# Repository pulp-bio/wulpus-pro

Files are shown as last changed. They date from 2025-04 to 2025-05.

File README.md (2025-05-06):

# WULPUS PRO v0.1.0
## A base platform for Wearable Ultra Low Power Ultrasound

# Introduction

This repository contains the work in progress on the WULPUS PRO ultrasound platform, a successor of the [WULPUS Project](https://github.com/pulp-bio/wulpus)

WULPUS PRO is a compact base platform for an ultra low power ultrasound sensing, featuring the following specifications:
- **16 channels** (time-multiplexed)
- **30 V** unipolar excitations with programmable frequency (100 kHz - 10 MHz)
- **Indirect and Direct Bias** (-30 V up to 30 V) for CMUT transducers
- **30.8 dB** Programable-Gain Amplifier + **80 dB** external VGA
- **Programmable** linear Time Gain Compesation Profiles
- **Optional** Envelope Extractor, runtime configurable
- **8 Msps** Analog-to-Digital converter (12 bit resolution)
- **SPI (8 MHz)** host MCU interface
- **Compactness and light weight** (40 x 20 mm footprint)
- **Ultra-Low Power** consumption of **<25 mW**

# WULPUS PRO system diagram

Work in progress.

# Structure of the repository

This repository has the following folders:

- `fw`, containing the firmware source code, namely:
    - source code for the nRF52832 MCU of the nRF52 DK, located at `fw/nrf52/ble_peripheral/US_probe_nRF52_firmware`
    - source code for the nRF52840 USB dongle, located at `fw/nrf52/peripheral/US_probe_dongle_firmware`
    - source code for the MSP430 ultrasound MCU, located at `fw/msp430`
- `sw`, containing the Python code for the WULPUS Pro Graphical User Interface
 
- `hw`, containing the CAD source files for 
    - WULPUS PRO Acquisition PCB (located at `hw/wulpus_pro_acq_pcb_dev_board`)
    - WULPUS adapter PCB for polyCMUT transducer (located at `hw/wulpus_polycmut_adapter`)

- `docs`, containing the project documentation (Work in Progress)

# Documentation 

WULPUS PRO build up on the top of the original WULPUS platfrom. Therefore, please refer to the original [WULPUS User Manual](docs/wulpus_user_manual.pdf) for assembly instructions, example measurements and GUI overview.

# How to reproduce?

To build and run your own instance of the **WULPUS PRO** platform, follow the steps below:

### 1. Manufacture and Assemble the Hardware

Produce the **WULPUS PRO acquisition development board** using the design files in:

- `hw/wulpus_pro_acq_pcb_dev_board`
- (Optionally) `hw/wulpus_polycmut_adapter`

Assemble the PCB using the provided schematics and BOMs.

### 2. Interconnect with nRF52 DK

Use the following pin mapping to connect the WULPUS PRO acquisition board to the **nRF52 DK**:

| **Signal**         | **nRF52 DK Pin** | **WULPUS PRO Connector Pin** |
|--------------------|------------------|-------------------------------|
| `SPI_SS`           | P0.04            | X3.4                          |
| `SPI_CLK`          | P0.29            | X3.3                          |
| `SPI_MISO`         | P0.30            | X3.1                          |
| `SPI_MOSI`         | P0.31            | X3.2                          |
| `Data_ready`       | P0.24            | X4.2                          |
| `BLE_conn_ready`   | P0.25            | X4.3                          |

### 3. Flash the MSP430 Firmware

Navigate to `fw/msp430/` and follow instructions to:

- Set up Code Composer Studio
- Compile the firmware
- Flash the MSP430 MCU

### 4. Flash the nRF52 DK and USB Dongle

Go to `fw/nrf52/` to:

- Set up Segger Studio and nRF Connect SDK
- Compile and flash:
  - nRF52832 DK (`ble_peripheral`)
  - nRF52840 USB dongle (`peripheral`)

### 5. Set Up the Python GUI

1. [Install Miniconda](https://docs.conda.io/en/latest/miniconda.html)
2. Go to the `sw` folder (contains `requirements.yml`)
3. Open terminal (Anaconda Prompt on Windows), run:
   ```bash
   conda env create -f requirements.yml
   conda activate wulpus_env
   jupyter notebook
   ```

## How to use?

To start a measurement with **WULPUS PRO**, follow these steps:

1. **Plug in the USB dongle** and **power the nRF52 DK** via USB.
2. **Check the dongle connection** (green LED should light up).  
   If not, press the **reset button on the nRF52 DK**, then try again.
3. **Only after confirming** dongle connectivity, **power the WULPUS PRO board** (via connector or debug pin headers).
4. Open a **Conda terminal**, activate the environment:
   ```bash
   conda activate wulpus_env
   ```

5. Then navigate to the `sw/` folder and open `wulpus_pro_gui.ipynb`. Follow the notebook instructions to begin acquisition.

# Authors

The WULPUS Pro system was developed at the [Integrated Systems Laboratory (IIS)](https://iis.ee.ethz.ch/) at ETH Zurich by:
- [Sergei Vostrikov](https://scholar.google.com/citations?user=a0KNUooAAAAJ&hl=en) (PCB design, Firmware, Software, Open-Sourcing)
- [Federico Villani](https://scholar.google.com/citations?user=5LgLMCEAAAAJ&hl=en) (PCB design, Component selection)
- [Cédric Hirschi](https://www.linkedin.com/in/c%C3%A9dric-cyril-hirschi-09624021b/) (Firmware, Software)
- [Andrea Cossettini](https://scholar.google.com/citations?user=d8O91jIAAAAJ&hl=en) (Supervision, Project administration)
- [Luca Benini](https://scholar.google.com/citations?hl=en&user=8riq3sYAAAAJ) (Supervision, Project administration)

Thanks to all the people who contributed to the WULPUS Pro platform:
- [Sebastian Frey](https://scholar.google.com/citations?user=7jhiqz4AAAAJ&hl=en) (Design review)

# License
The following files are released under Apache License 2.0 (`Apache-2.0`) (see `sw/LICENSE`):

- `sw/`

The following files are released under Solderpad v0.51 (`SHL-0.51`) (see `hw/LICENSE`):

- `hw/`

The `fw/msp430/` and `fw/nrf52/` directories contain third-party sources that come with their own
licenses. See the respective folders and source files for the licenses used.

## Limitation of Liability
In no event and under no legal theory, whether in tort (including negligence), contract, or otherwise, unless required by applicable law (such as deliberate and grossly negligent acts) or agreed to in writing, shall any Contributor be liable to You for damages, including any direct, indirect, special, incidental, or consequential damages of any character arising as a result of this License or out of the use or inability to use the Work (including but not limited to damages for loss of goodwill, work stoppage, computer failure or malfunction, or any and all other commercial damages or losses), even if such Contributor has been advised of the possibility of such damages.

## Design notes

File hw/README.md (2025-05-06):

# WULPUS PRO PCB design files
This directory contains the design files for the printed circuit boards (PCBs) of the WULPUS PRO project.
Each subdirectory corresponds to a separate PCB project. Inside you can find the Altium CAD design files:
- Source design files
- PDF schematics and assembly drawings (`docs` folder), 
- Fabrication outputs (`fabrication_outputs` folder):
    - Bill of Materials(.xlsx) 
    - Gerber files
    - NC drill files
    - Pick and Place files

# License
The PCB design files are licensed under Solderpad v0.51 (`SHL-0.51`) license. Please, check the `hw/LICENSE` file for details.

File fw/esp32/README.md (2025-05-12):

# WULPUS PRO ESP32 Firmware

This firmware enables WULPUS PRO to connect to Wi-Fi via a ESP32-C6, which enables higher throughputs and thus framerates.

The firmware includes the following features:
- **mDNS**: Multicast DNS for local network discovery
- **Full integration with the Python API**: The firmware also comes with an extension to the Python API, which allows you to control the WULPUS PRO over Wi-Fi
- **Power Management**: The firmware includes power management, which allows the ESP32 to enter light sleep when not in use. This results in ~1.5mA current draw
- **Easy expandability**: The firmware is designed to be easily extensible, allowing you to add new features and functionality as needed

## Getting Started

This firmware is written with [ESP-IDF](https://github.com/espressif/esp-idf). We recommend using at the official [VS Code extension](https://github.com/espressif/vscode-esp-idf-extension/tree/master).

The firmware is tested on the [ESP32-C6-DEVKITM-1](https://docs.espressif.com/projects/esp-dev-kits/en/latest/esp32c6/esp32-c6-devkitm-1/user_guide.html) board, but should work on any ESP32-C6 board. The firmware is designed to be easily portable to other ESP32 boards as well.

### Connection to WULPUS PRO

Use the following pin mapping to connect the WULPUS PRO acquisition board to the **ESP32-C6-DEVKITM-1**:

| **Signal**         | **ESP32-C6 Pin** | **WULPUS PRO Connector Pin**  |
|--------------------|------------------|-------------------------------|
| `SPI_SS`           | 18               | X3.4                          |
| `SPI_CLK`          | 6                | X3.3                          |
| `SPI_MISO`         | 7                | X3.1                          |
| `SPI_MOSI`         | 2                | X3.2                          |
| `Data_ready`       | 1                | X4.2                          |
| `BLE_conn_ready`   | 0                | X4.3                          |

These pins can be changed however you like by using the [SDK Configurator](https://docs.espressif.com/projects/vscode-esp-idf-extension/en/latest/configureproject.html).

### Usage in the Python API

The Python API remains largely unchanged, the only thing you need to do in order to use the Wi-Fi connection is to pass the `WulpusWiFi` communication link to the `WulpusGuiSingleCh` class instead of the `WulpusDongle` class. This will look like this:

```python
from wulpus.wifi import WulpusWiFi

# Create a wifi object
wifi = WulpusWiFi()

# Setup the GUI (uss_conf is already setup and configured)
gui = WulpusGuiSingleCh(wifi, uss_conf)

display(gui)
```

## TODO

This firmware is still a work in progress. The following features are planned for future releases (among others):

- [ ] Add LED status codes
- [ ] Return error codes on the socket on failures

## Licensing

ESP-IDF is licensed under the Apache License 2.0. See the [LICENSE](https://github.com/espressif/esp-idf/blob/master/LICENSE) in the ESP-IDF repository for more information.

ESP-IDF uses multiple third-party components, which are licensed under various other open-source licenses. One example is [FreeRTOS](https://github.com/FreeRTOS). Please make sure all of the licenses are compatible with your project.

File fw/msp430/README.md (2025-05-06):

# WULPUS PRO source files for MSP430 Ultrasound MCU firmware project
This directory contains the source firmware files for 
- MSP430FR5043 Ultrasound MCU (`fw/msp430/wulpus_msp430_firmware`) mounted on the WULPUS PRO PCB

# How to get started?

Please refer to the `WULPUS User Manual` of the WULPUS system v 1.2.2 for the instructions on how to flash the MSP430 MCU:
`https://github.com/pulp-bio/wulpus/blob/main/docs/wulpus_user_manual.pdf`

# License
The files in the `hw/nRF52/wulpus_msp430_firmware` directory contains third-party sources that come with their own licenses (primarily BSD and Apache 2.0 License). See the respective folders and source files' headers for the licenses used.

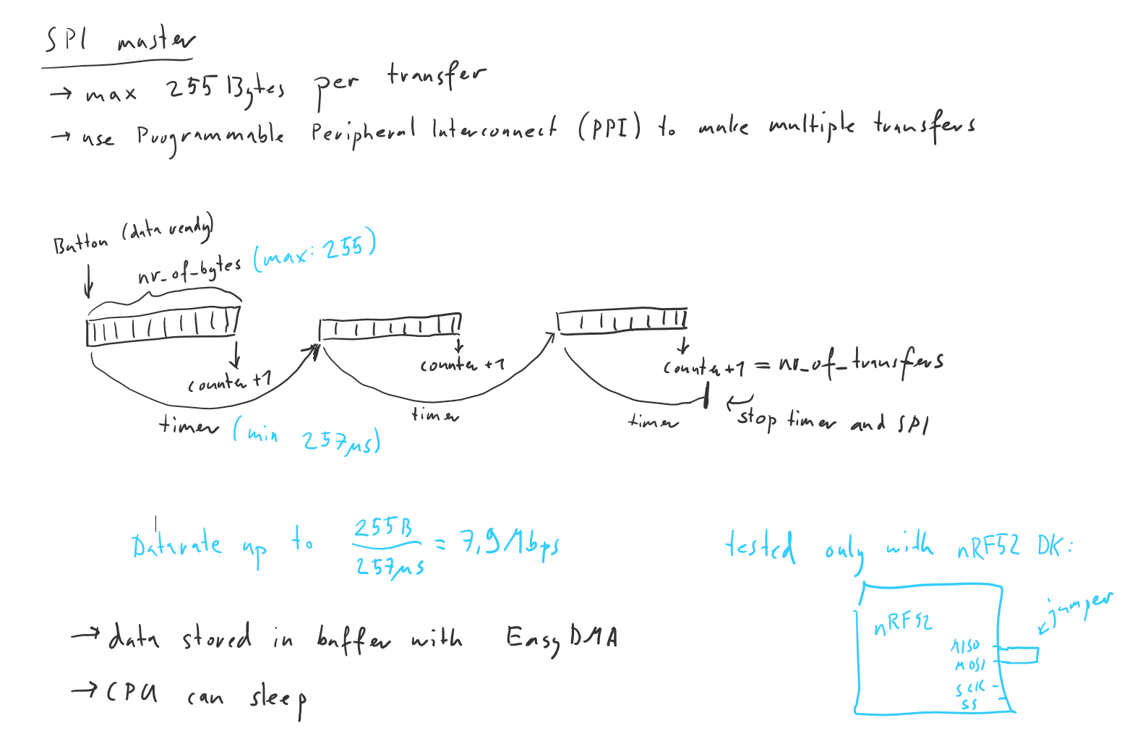
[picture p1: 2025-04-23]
fw/nrf52/ble_peripheral/US_probe_nRF52_firmware/Explanation_of_SPI_transaction.PNG

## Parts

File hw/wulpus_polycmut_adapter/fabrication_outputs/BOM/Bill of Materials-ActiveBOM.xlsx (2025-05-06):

Designator | Name | Manufacturer Part Number 1 | Description | Quantity
J3, J4 | 91910-21169LF |  |  | 2
P1 | polycmut |  |  | 1
R1, R2, R3, R4, R5, R6, R7, R8 | RC0402JR-070RL | CR0402-J/-000GLF |  | 8
J5 | 901-144-8RFX | 901-144-8RFX | Coaxial Connector, 18 GHz, 50 Ohm, -65 to 165 degC, 5-Pin THD, RoHS, Bulk | 1

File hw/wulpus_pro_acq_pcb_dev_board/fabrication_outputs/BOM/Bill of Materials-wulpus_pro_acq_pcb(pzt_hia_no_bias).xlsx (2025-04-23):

Designator | Name | Manufacturer Part Number 1 | Description | Quantity
C2, C17, C18, C19, C21, C22, C23, C29, C31, C33, C51, C52, C53, C73, C74, C75, C76 | C0402C104K4RACTU | GRM155R71C104KA88D |  | 17
C24, C25 | GRM1555C1H100JA01D | GRM1555C1H100JA01D |  | 2
PJ1 | 5051100892 |  |  | 1
R35, R38 | RC0402JR-0722RL | RC0402JR-0722RL |  | 2
R36 | CPF0402B324RE1 | CPF0402B324RE1 |  | 1
U13 | MD0100N8-G |  |  | 1
X5, X6, X7, X8 | 68000-102HLF | 68000-102HLF | 2 Positions Header, Unshrouded Connector 0.100" (2.54mm) Through Hole Gold or Gold, GXT™ | 4
X1, X3, X4 | 68000-106HLF | 68000-106HLF | 6 Positions Header, Unshrouded Connector 0.100" (2.54mm) Through Hole Gold or Gold, GXT™ | 3
U11 | HV2707T-C/R8X |  | 16-CH 200V No Hv Bias Switch (SPST), 2 Bleed Resistor 48 LQFP 7X7X1.4MM T/r Rohs Compliant: Yes | 1
R9 | RMCF0201JT47K0 | RMCF0201JT47K0 | 47kΩ ±5% 0.05W 0201 Thick Film Chip Resistor AEC-Q200 compliant | 1
J12 | DF40HC(3.0)-50DS-0.4V(51) |  | 50 Position 0.4mm Pitch Dual Row Vertical Surface Mount (SMT) Pin Socket, 3.0mm Stacking Height | 1
U3 | TPL0501-100RSER | TPL0501-100RSER | 256-Tap, 100 k, Single Channel Potentiometer with SPI Interface, -40 to 125 degC, 8-pin QFN (RSE8), Green (RoHS & no Sb/Br) | 1
U4, U7 | TS5A3159AYZPR |  | Analogue Switch ICs SPDT ANALOG SWITCH | 2
FB3, FB4 | BLM18SP101SH1D | BLM18SP101SH1D | BLM18SP101SH1D Ferrite Beads Multi-Layer 100Ohm 25% 100MHz 3.7A 0.022Ohm DCR 0603 Automotive T/R | 2
FB1, FB2 | BLM18SP101SN1D | BLM18SP101SN1D | BLM18SP101SN1D Ferrite Bead, 100 Ohm, 3.7A, 0603 Rohs Compliant: Yes |Murata BLM18SP101SN1D | 2
C8, C9, C11, C14, C15, C20, C28, C30, C32, C40, C48, C49, C50 | C1005X7S1A225K050BC | C1005X7S1A225K050BC | CAP CER 2.2UF 10V X7S 0402 | 13
C64 | GCM21BR71H105KA03L | GCM21BR71H105KA03L | Ceramic Capacitor for Automotive 1uF ±10% 50VDC X7R 0805 Embossed T/R | 1
C3, C6 | GRM033R71A103KA01D | GRM033R71A103KA01D | Chip Multilayer Ceramic Capacitors for General Purpose, 0201, 10000pF, X7R, 15%, 10%, 10V | 2
C67 | GRM155C71H104KE19D | GRM155C71H104KE19D | Chip Multilayer Ceramic Capacitors for General Purpose, 0402, 0.10uF, X7S, 22%, 10%, 50V | 1
C69, C70, C71, C72 | GRM155Z71A105KE01D | GRM155Z71A105KE01D | Chip Multilayer Ceramic Capacitors for General Purpose, 0402, 1.0uF, X7R, 15%, 10%, 10V | 4
C4, C7, C10, C43, C45, C46, C56 | GRM1555C1H102JA01D | GRM1555C1H102JA01D | Chip Multilayer Ceramic Capacitors for General Purpose, 0402, 1000pF, C0G, 30ppm/°C, 5%, 50V | 7
C41, C42 | GRM155R71H473ME14D | GRM155R71H473ME14D | Chip Multilayer Ceramic Capacitors for General Purpose, 0402, 47000pF, X7R, 15%, 20%, 50V | 2
C26, C34, C35, C36, C37, C38, C39, C61, C62, C63, C65, C66, C68 | GRM188R61H225ME11D | GRM188R61H225ME11D | Chip Multilayer Ceramic Capacitors for General Purpose, 0603, 2.2uF, X5R, 15%, 20%, 50V | 13
J1, J2 | DF40C-40DS-0.4V(51) | DF40C-40DS-0.4V(51) | CONN RCPT 40POS SMD GOLD | 2
J10, J11 | U.FL-R-SMT-1(10) | U.FL-R-SMT-1(10) | CONN U.FL RCPT STR 50 OHM SMD | 2
J3, J5 | 91931-31169LF |  | Conn; Rect; Industrial; MezzanineRECP; 69Cnts; SMT; I-IndustrialSeries | 2
R4, R21, R33, R34 | CRCW04021R00FKEDC | CRCW04021R00FKEDC | CRCW04021R00FKEDC Res Thick Film 0402 1 Ohm 1% 1/16W ±100ppm/°C Molded SMD Paper T/R | 4
X2 | FY0800018 | FY0800018 | Crystal 8MHz ±30ppm (Tol) ±30ppm (Stability) 18pF FUND 100Ohm 4-Pin SMD T/R | 1
Y2 | ABS05-32.768KHZ-9-T | ABS05-32.768KHZ-9-T | CRYSTAL 32.7680KHZ 9PF SMD | 1
D1 | BAV99T-7-F | BAV99T-7-F | DIODE ARRAY GP 85V 75MA SOT523 | 1
D3 | ZHCS400QTA | ZHCS400QTA | Diode Schottky 40V 1A Automotive 2-Pin SOD-323 T/R | 1
U15 | LT3463AEDD#PBF | LT3463AEDD#PBF | Dual Micropower DC/DC Converters with Schottky Diodes, 2.4 to 15 V Vin, 10-pin SON (DD-10), -40 to 85 degC, Pb-Free | 1
R39, R42 | 1MΩ |  | ERJ-2RKF1004X | 2
R41 | 41.2 kΩ |  | ERJ-2RKF4122X | 1
R40 | 43.2 kΩ |  | ERJ-2RKF4322X | 1
R24 | 3k 1/3W |  | ERJ-PA3J302V | 1
C5 | 04025C332JAT2A | 04025C332JAT2A | General Purpose Ceramic Capacitor, 0402, 3.3nF, 5%, X7R, 15%, 50V | 1
C13, C27 | 04025A101FAT2A | 04025A101FAT2A | General Purpose Ceramic Capacitor, 0402, 100pF, 1%, C0G, 30ppm/°C, 50V | 2
C16, C44, C47 | GRM188R60J476ME01D | GRM188R60J476ME01D | GRM188R60J476ME01D Ceramic Capacitor, Multilayer, Ceramic, 6.3V, 20% +Tol, 20% -Tol, X5R, 15% TC, 47uF, Surface Mount, 0603 | 3
U1 | AD8338ACPZ-R7 | AD8338ACPZ-R7 | IC OPAMP VGA 1 CIRCUIT 16LFCSP | 1
U5 | LTC5507ES6#TRMPBF | LTC5507ES6#TRMPBF | IC RF DETECT 100KHZ-1GHZ TSOT23 | 1
U9 | IXDD604D2TR |  | Integrated Circuit | 1
D2 | APHD1608LZGCK | APHD1608LZGCK | LED GREEN CLEAR 1608 SMD | 1
Q1 | NX7002BKMBYL |  | MOSFET (N-Channel) | 1
C1 | GJM1555C1H1R5BB01D | GJM1555C1H1R5BB01D | Multi-Layer Ceramic Capacitor 1.5pF C0G ±0.1pF 0402 Paper T/R | 1
C54, C55, C57, C58, C59, C60 | GJM1555C1H120GB01D | GJM1555C1H120GB01D | Multi-Layer Ceramic Capacitor 12pF C0G ±2% 0402 Paper T/R | 6
J4, J6 | DF52-16S-0.8H(21) |  | No Description Available | 2
U14 | MSP430FR5043IRGCT |  | No Description Available | 1
Y1 | AWSCR-8.00CV-T |  | No Description Available | 1
R15 | ERJ-3GEY0R00V | ERJ-3GEY0R00V | RES SMD 0 OHM JUMPER 1/10W 0603 | 1
R5 | MCS04020C2701FE000 | MCS04020C2701FE000 | RES SMD 1.2K OHM 1% 1/10W 0402 | 1
R2, R3 | ERJ-2RKF2001X | ERJ-2RKF2001X | RES SMD 2K OHM 1% 1/10W 0402 | 2
R27, R28 | ERJ-2RKF1003X | ERJ-2RKF1003X | RES SMD 100K OHM 1% 1/10W 0402 | 2
R26, R29 | RC1005F394CS | RC1005F394CS | Res Thick Film 0402 390kΩ 1% 0.063W ±100ppm/°C Molded SMD T/R | 2
R8, R18, R23, R45, R47 | CRCW04020000Z0ED | CRCW04020000Z0ED | RES Thick Film, 0Ω, 0.063W, 0402 | 5
R31, R32 | CRCW04021M00FKED | CRCW04021M00FKED | RES Thick Film, 1MΩ, 1%, 0.063W, 100ppm/°C, 0402 | 2
R1 | CRCW04021K30JNED | CR0402-JW-132GLF | RES Thick Film, 1.3kΩ, 5%, 0.063W, 200ppm/°C, 0402 | 1
R10, R11, R12, R14, R16, R22, R43, R44 | CRCW040210K0JNED | CRCW040210K0JNED | RES Thick Film, 10kΩ, 5%, 0.063W, 200ppm/°C, 0402 | 8
R37 | CRCW040247K0FKED | CRCW040247K0FKED | RES Thick Film, 47kΩ, 1%, 0.063W, 100ppm/°C, 0402 | 1
R13 | CRCW040251R0JNED | CRCW040251R0JNED | RES Thick Film, 51Ω, 5%, 0.063W, 200ppm/°C, 0402 | 1
L1, L2 | 742792040 | 742792040 | SMD EMI Suppression Ferrite Bead WE-CBF, Z = 600 Ohm | 2
U6, U8, U12, U16 | TPS22916CYFPR |  | TPS22916 5.5-V, 2-A Ultra-Low Leakage Load Switch | 4
U2, U10 | OPA836IDBVT |  | Very Low Power, Rail to Rail Out, Negative Rail In, VFB Operational Amplifier, 2.5 to 5.5 V, -40 to 125 degC, 6-pin SOT23 (DBV6), Green (RoHS & no Sb/Br) | 2
U17, U18 | SN74AVC4T774RSVR |  | Voltage Level Translator Bidirectional 1 Circuit 4 Channel 380Mbps 16-UQFN _2.6x1.8_ | 2
L3, L4 | LQH3NPZ100MMEL | LQH3NPZ100MMEL | Wire Wound Ferrite Inductor for Power Lines For Automotive 10μH ±20% 0.228Ω 1280mA 1212 | 2

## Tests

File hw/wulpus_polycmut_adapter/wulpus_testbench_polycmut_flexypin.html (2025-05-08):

Reporting Options

# File in Newer Format

Date | : | 07/05/2025
Time | : | 12:06:18
Filename | : | C:\Users\serge\Documents\repos\wulpus-pro\hw\wulpus_polycmut_adapter\wulpus_testbench_polycmut_flexypin.PrjPcb

Version | Warning

Release 23.10

CAUTION - This project contains rules defined using the Constraint Manager. You are seeing this message for two possible reasons. Firstly, this is an older version of the software that does not support this feature, in which case design rules will fall back to being presented as standard, query-based rules. If you save the PCB project in this older version of Altium Designer, all Constraint Manager data structure information will be lost. Secondly, if this software version does support the feature, then you currently don't have the level of Altium Designer Software Subscription (Pro/Enterprise) to be able to edit constraints using the Constraint Manager, in which case it will present rules in view only mode.

This file was generated by a later version of the software

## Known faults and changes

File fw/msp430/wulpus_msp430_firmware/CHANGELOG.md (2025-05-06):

# Changelog

All notable changes to this project will be documented in this file.

The format is based on [Keep a Changelog](https://keepachangelog.com/en/1.0.0/),
and this project adheres to [Semantic Versioning](https://semver.org/spec/v2.0.0.html).

## [Unreleased] - 2025-05-01

### Added

- MSP 430 firmware from WULPUS repository version 1.2.2

### Fixed

### Changed
- Changed pin mapping of the pins according to the schematics of the WULPUS PRO
- Added initialization of multiple new IOs for enbaling power domain and VGA control
- Added two new configuration parameters to the `msp_config` for VGA control:
    - `VGA Precharge time`
    - `Wiper code for gain slope`

- Added a new timer instance for precise time delay for VGA control input precharging.

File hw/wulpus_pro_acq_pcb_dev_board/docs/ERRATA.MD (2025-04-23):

# Violations of reference circuits
- Power switch U16 should have at least 1 uF input capacitance. It is not placed in v1.0.0

# Bugs
- The MSP430 programming connector PJ1 has a swapped (symmetrically mirrored) pin mapping compared to the WULPUS v1.2.2 design.
 That make the corresponding adapter PCBs incompatible with WULPUS pro design (requires the FPC cable that also swaps the pins symmetrically).

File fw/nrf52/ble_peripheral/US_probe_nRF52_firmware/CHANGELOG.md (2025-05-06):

# Changelog

All notable changes to this project will be documented in this file.

The format is based on [Keep a Changelog](https://keepachangelog.com/en/1.0.0/),
and this project adheres to [Semantic Versioning](https://semver.org/spec/v2.0.0.html).

## [Unreleased] - 2025-05-01

### Added

- nRF52832 firmware from WULPUS repository version 1.2.2

### Fixed

### Changed
- Changed pin mapping of the SPI and supplementary (`HOST_READY`, `DATA_READY`) pins according to the schematics of the WULPUS PRO and connection to the nRF52 DK (see main README).
- Decreased the SPI frequency to 2 MHz for better signal integrity while testing with the wire jumpers interconnecting the PCBs.

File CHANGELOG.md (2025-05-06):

# Changelog

All main changes to this project will be documented in this file.
For the detailed description, please explore nested folders and corresponding CHANGELOG.md files (e.g. for PCB projects or firmware). 

The format is based on [Keep a Changelog](https://keepachangelog.com/en/1.0.0/),
and this project adheres to [Semantic Versioning](https://semver.org/spec/v2.0.0.html).

## [0.1.0] - 2025-05-1

### Added

### Fixed

### Changed

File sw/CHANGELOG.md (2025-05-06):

# Changelog

All notable changes to this project will be documented in this file.

The format is based on [Keep a Changelog](https://keepachangelog.com/en/1.0.0/),
and this project adheres to [Semantic Versioning](https://semver.org/spec/v2.0.0.html).

## [Unreleased] - 2025-05-01

### Added

- GUI and library from WULPUS repository version 1.2.2
- A curve to the main GUI, visualizing the gain profile over time.

### Fixed

### Changed

- Extended the number of channels to 16.
- Modified TX/RX pin mapping.
- Added two new configuration parameters for VGA control:
    - `VGA Precharge time [cycles]`
    - `Wiper code for gain slope []`

- Extended the configuration package to accomodate two new parameters.

### Removed
- Removed `Capture restart time` and `Capture timeout time` from the old GUI.

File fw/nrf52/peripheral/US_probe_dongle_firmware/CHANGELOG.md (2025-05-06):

# Changelog

All notable changes to this project will be documented in this file.

The format is based on [Keep a Changelog](https://keepachangelog.com/en/1.0.0/),
and this project adheres to [Semantic Versioning](https://semver.org/spec/v2.0.0.html).

## [Unreleased] - 2025-05-01

### Added

- nRF52840 firmware for nRF Dongle from WULPUS repository version 1.2.2

### Fixed

### Changed
- Changed the size of the configuration package from 68 to 72 bytes to accomodate new parameters.

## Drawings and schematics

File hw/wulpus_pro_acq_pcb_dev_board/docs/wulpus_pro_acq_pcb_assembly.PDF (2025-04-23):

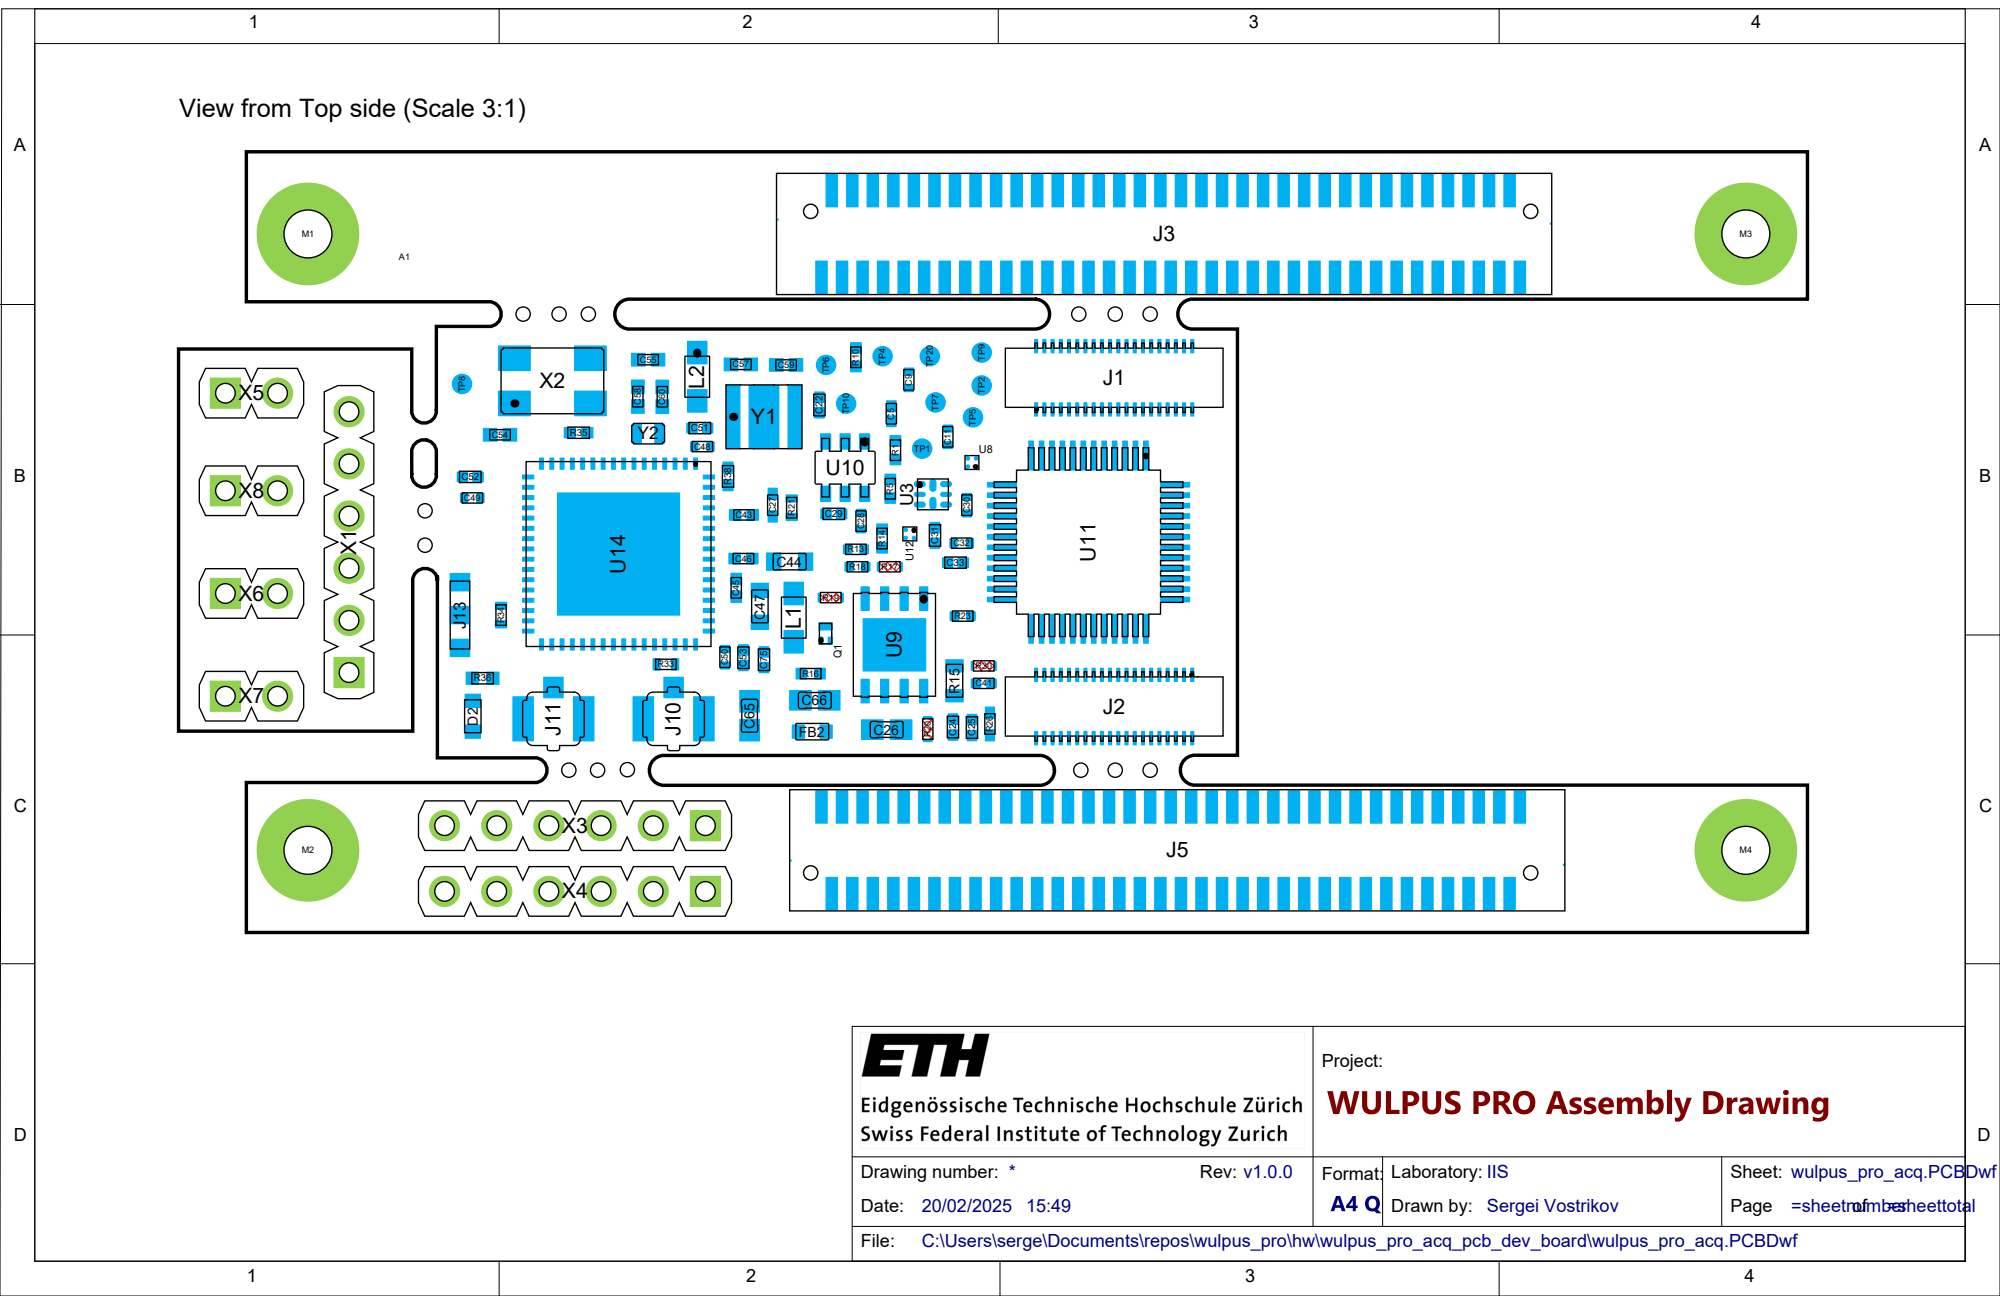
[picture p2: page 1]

View from Top side (Scale 3:1)

Project:

Drawing number: * Rev: v1.0.0 Date: | Format: | Laboratory: IIS Drawn by: Sergei Vostrikov | Sheet: wulpus_pro_acq.PCBDwf Page =sheetnumber of =sheettotal

C:\Users\serge\Documents\repos\wulpus_pro\hw\wulpus_pro_acq_pcb_dev_board\wulpus_pro_acq.PCBDwf

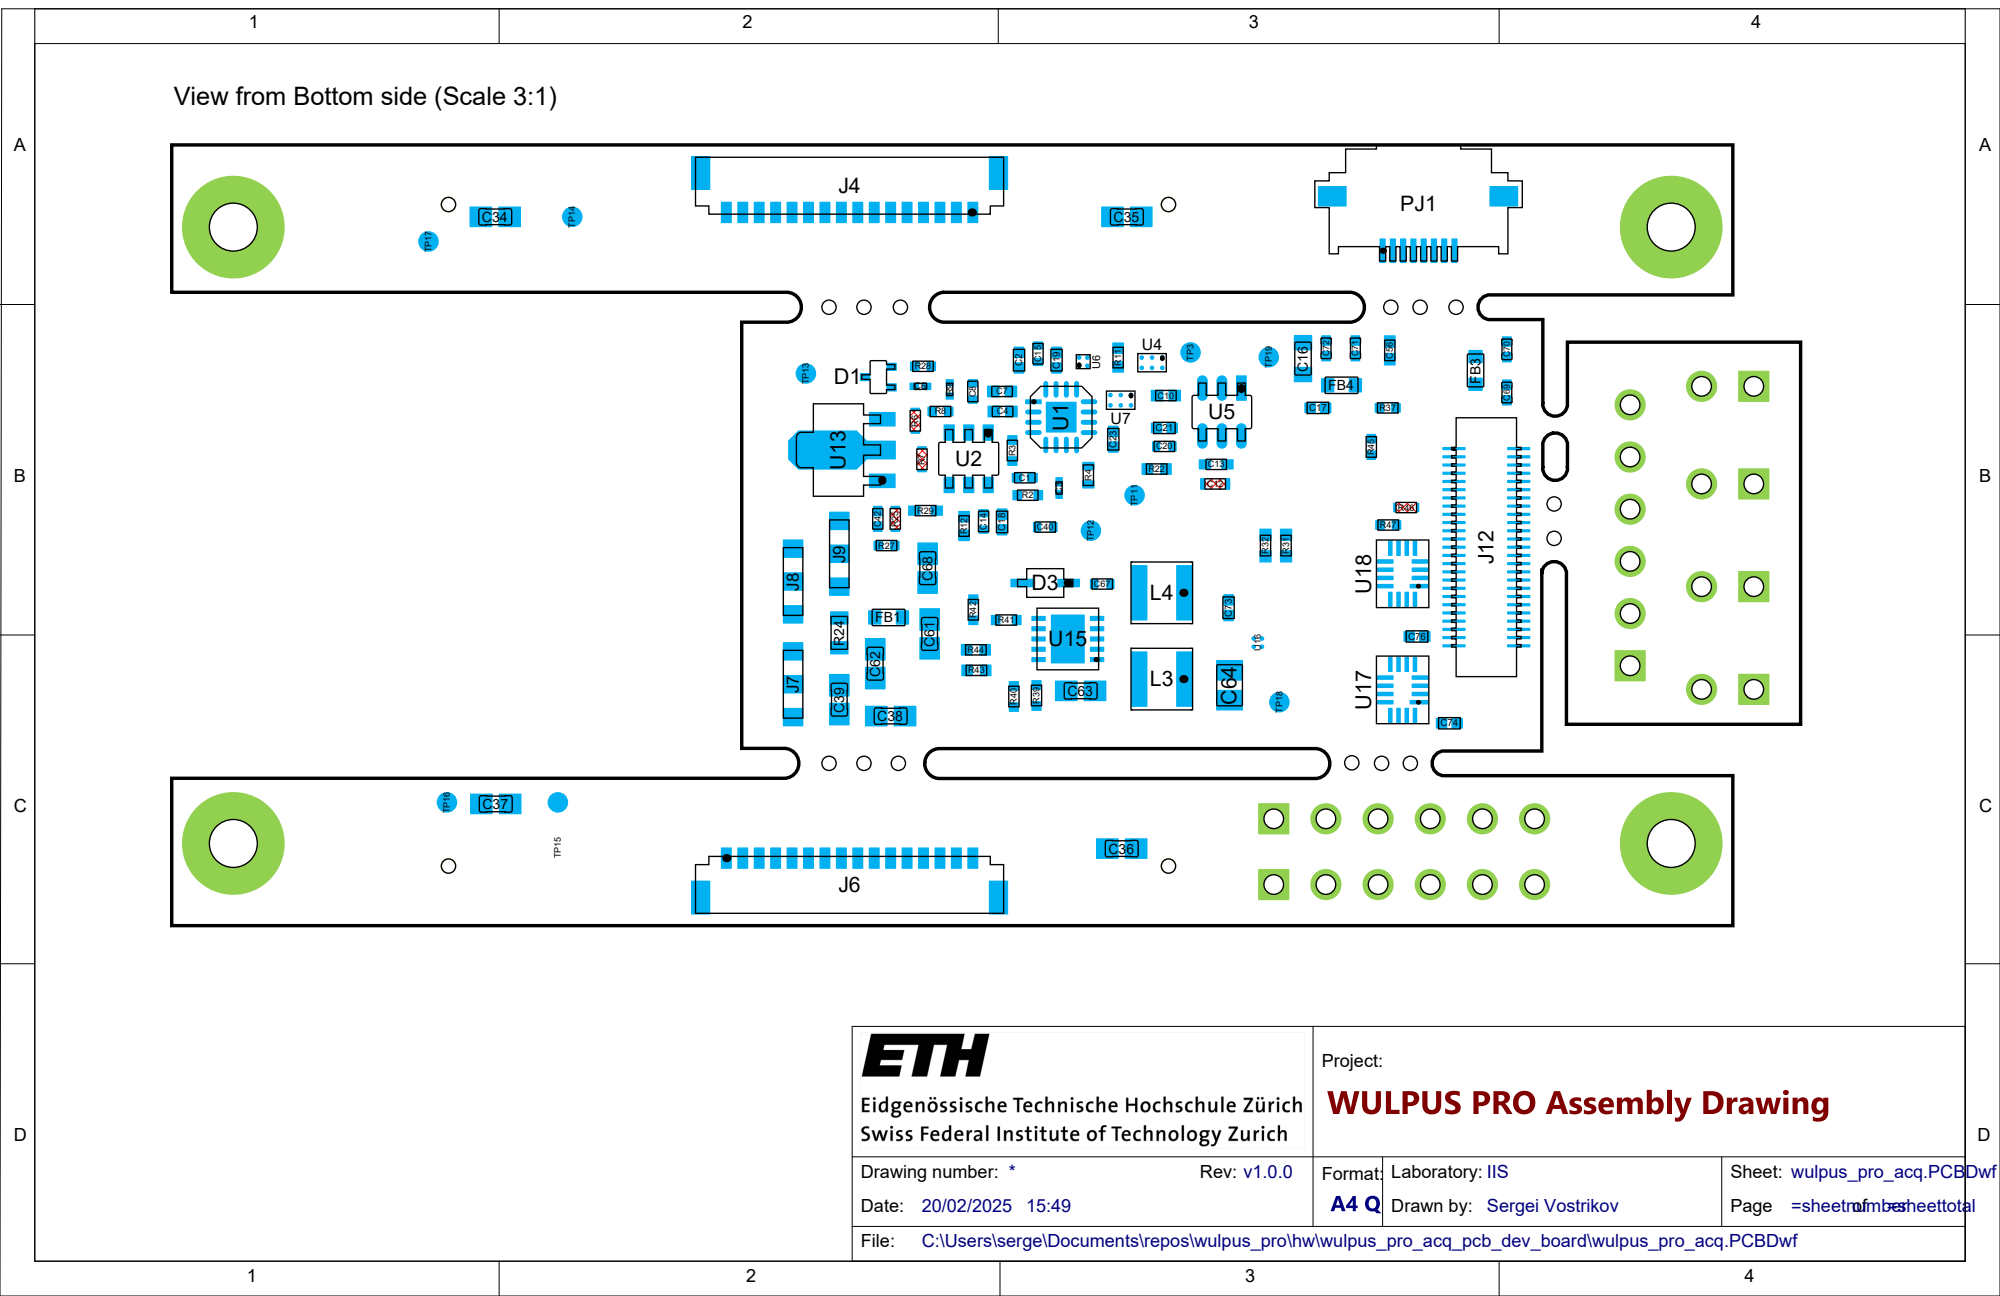
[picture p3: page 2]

View from Bottom side (Scale 3:1)

Project:

Drawing number: * Rev: v1.0.0 | Format: | Laboratory: IIS | Sheet: wulpus_pro_acq.PCBDwf

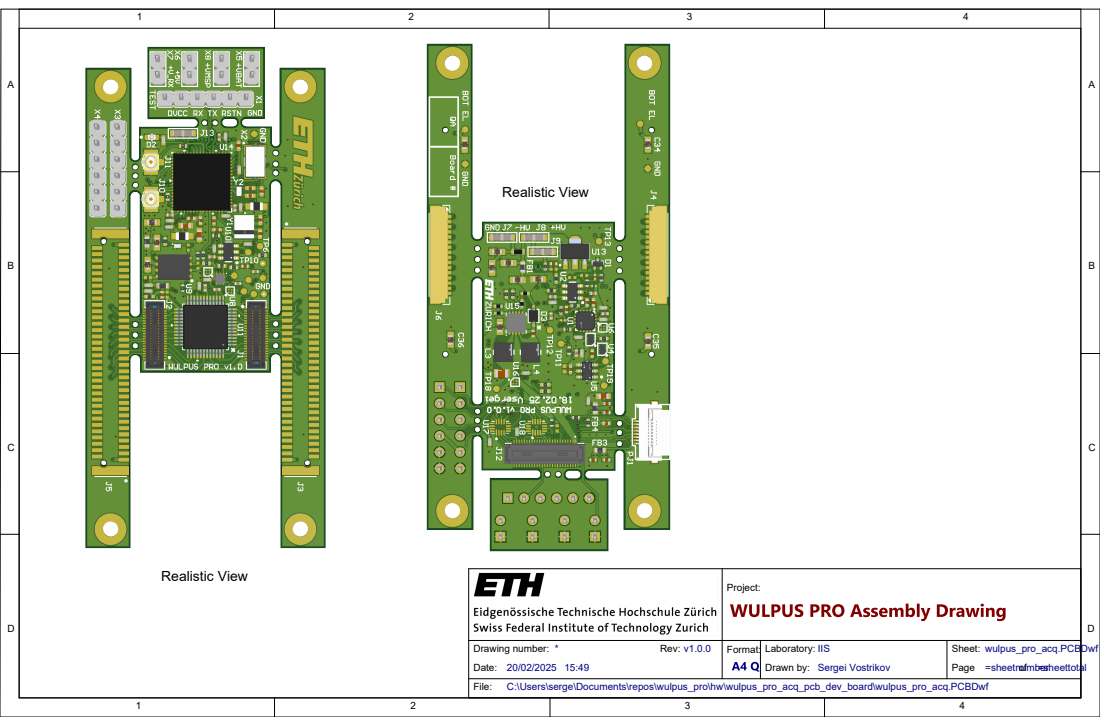
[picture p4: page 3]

Project:

Drawing number: * Rev: v1.0.0 | Format: | Laboratory: IIS | Sheet: wulpus_pro_acq.PCBDwf

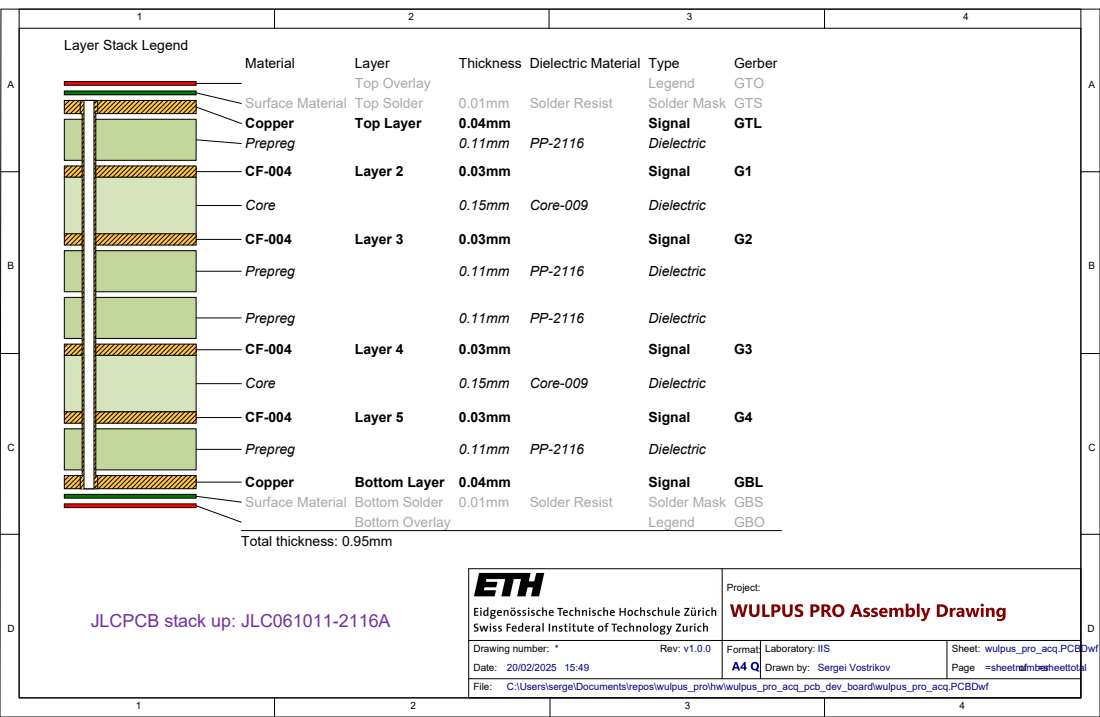
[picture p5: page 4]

Project:

Drawing number: * Rev: v1.0.0 | Format: | Laboratory: IIS | Sheet: wulpus_pro_acq.PCBDwf

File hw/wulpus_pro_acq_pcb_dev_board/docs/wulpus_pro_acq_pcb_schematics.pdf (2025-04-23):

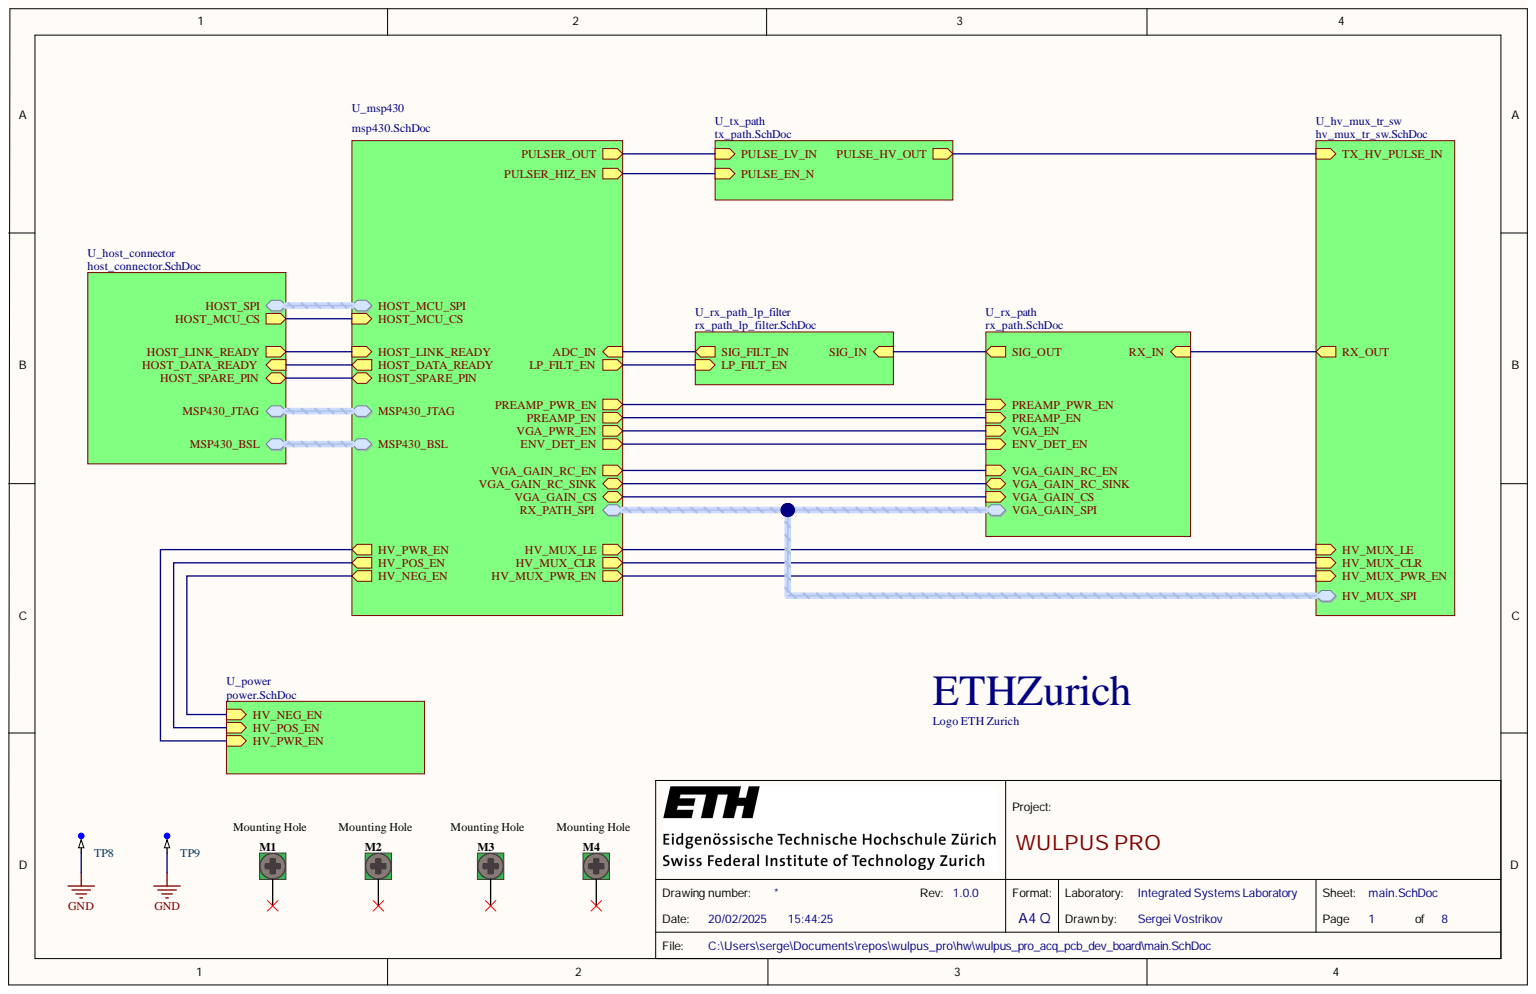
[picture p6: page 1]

Proje c t: W U L P U S P R O

Drawing numbe r: * R e v : 1. 0. 0 D a te : 20/02/202 5 15:44 : 2 5 | Form a t: A 4 Q | Laborato ry : Integrated Sy s tem s Labora to ry Drawn by : Sergei Vos trik ov | Shee t: main. S c h D o c Pag e 1 of 8

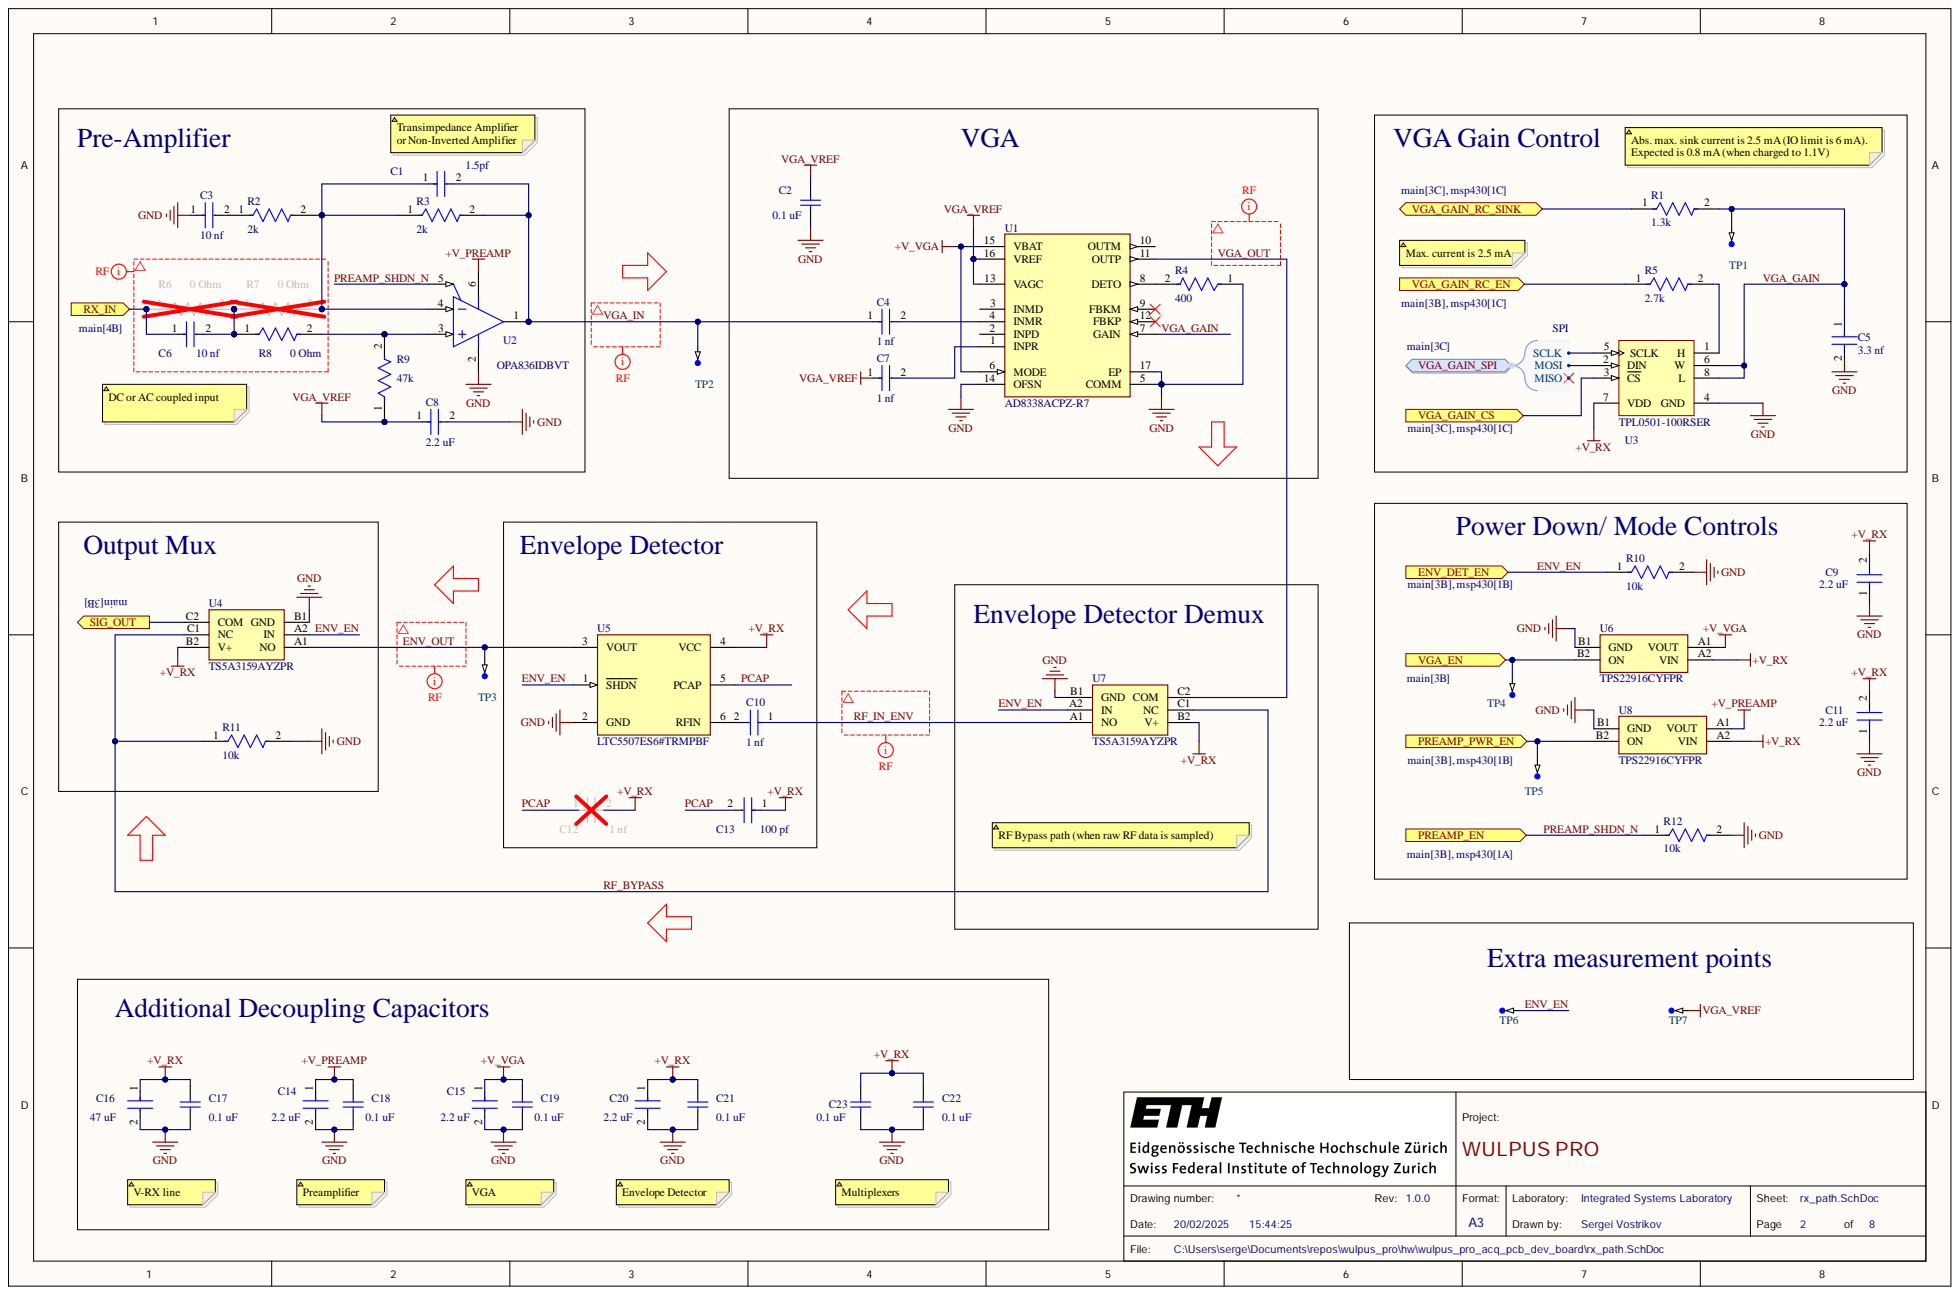
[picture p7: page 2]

Expected is 0.8 mA(when charged to 1.1V)

Max. current is 2.5 mA

DC or AC coupled input

Power Down/ Mode Controls

RF Bypass path (when raw RF data is sampled)

Project: WULPUS PRO

Drawing number: * Rev: 1.0.0 Date: 15:44:25 | Format: A3 | Laboratory: Integrated Systems Laboratory Drawn by: Sergei Vostrikov | Sheet: rx_path.SchDoc Page 2 of 8

C:\Users\serge\Documents\repos\wulpus_pro\hw\wulpus_pro_acq_pcb_dev_board\rx_path.SchDoc

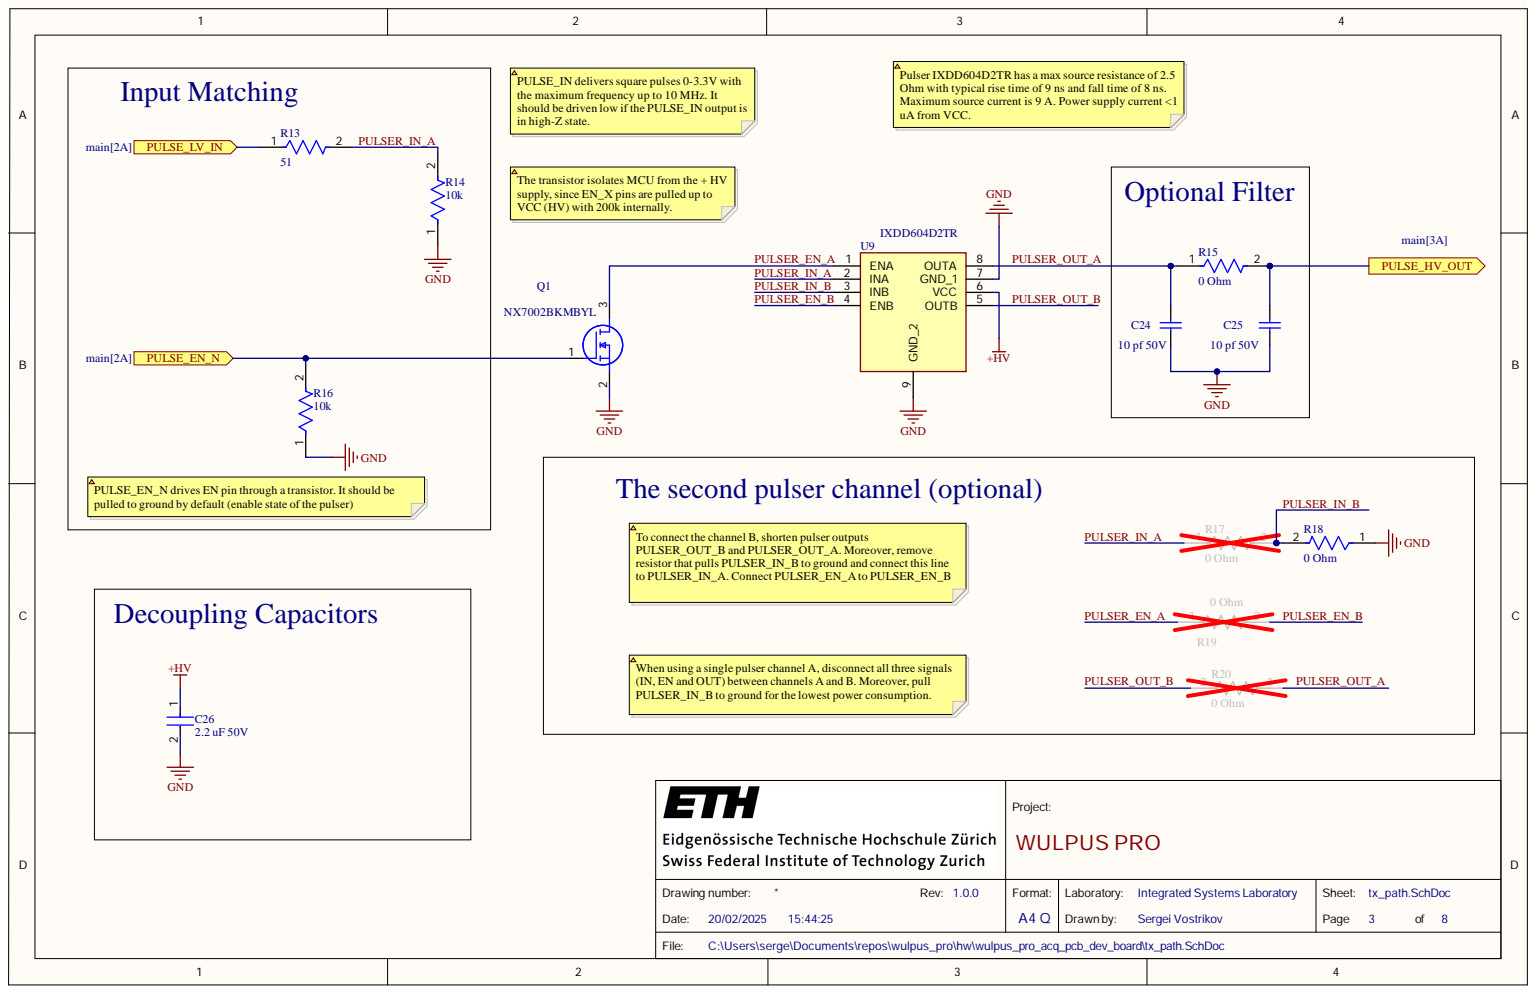
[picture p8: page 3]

PULSE_IN deliverssquare pulses 0-3.3V with
the maximum frequency up to 10 MHz. It
should be driven low if the PULSE_IN output is
in high-Z state.

Pulser IXDD604D2TR has a max source resistance of 2.5
Ohm with typical rise time of 9 ns and fall time of 8 ns.
Maximum source current is 9 A. Power supply current <1
uA from VCC.

The transistor isolates MCU from the + HV
supply, since EN_X pins are pulled up to
VCC (HV) with 200k internally.

PULSE_EN_N drives EN pin through a transistor. Itshould be
pulled to ground by default (enable state of the pulser)

The second pulser channel (optional)

To connect the channel B, shorten pulser outputs
PULSER_OUT_B and PULSER_OUT_A. Moreover, remove
resistor that pulls PULSER_IN_B to ground and connect this line
to PULSER_IN_A. Connect PULSER_EN_A to PULSER_EN_B

Decoupling Capacitors +HV | C26

When using a single pulser channel A, disconnect all three signals
(IN, EN and OUT) between channels A and B. Moreover, pull
PULSER_IN_B to ground for the lowest power consumption.

Project: WULPUS PRO

Drawing number: * Rev: 1.0.0 Date: 20/02/2025 15:44:25 | Format: A4 Q | Laboratory: Integrated Systems Laboratory Drawn by: Sergei Vostrikov | Sheet: tx_path.SchDoc Page 3 of 8

C:\Users\serge\Documents\repos\wulpus_pro\hw\wulpus_pro_acq_pcb_dev_board\tx_path.SchDoc

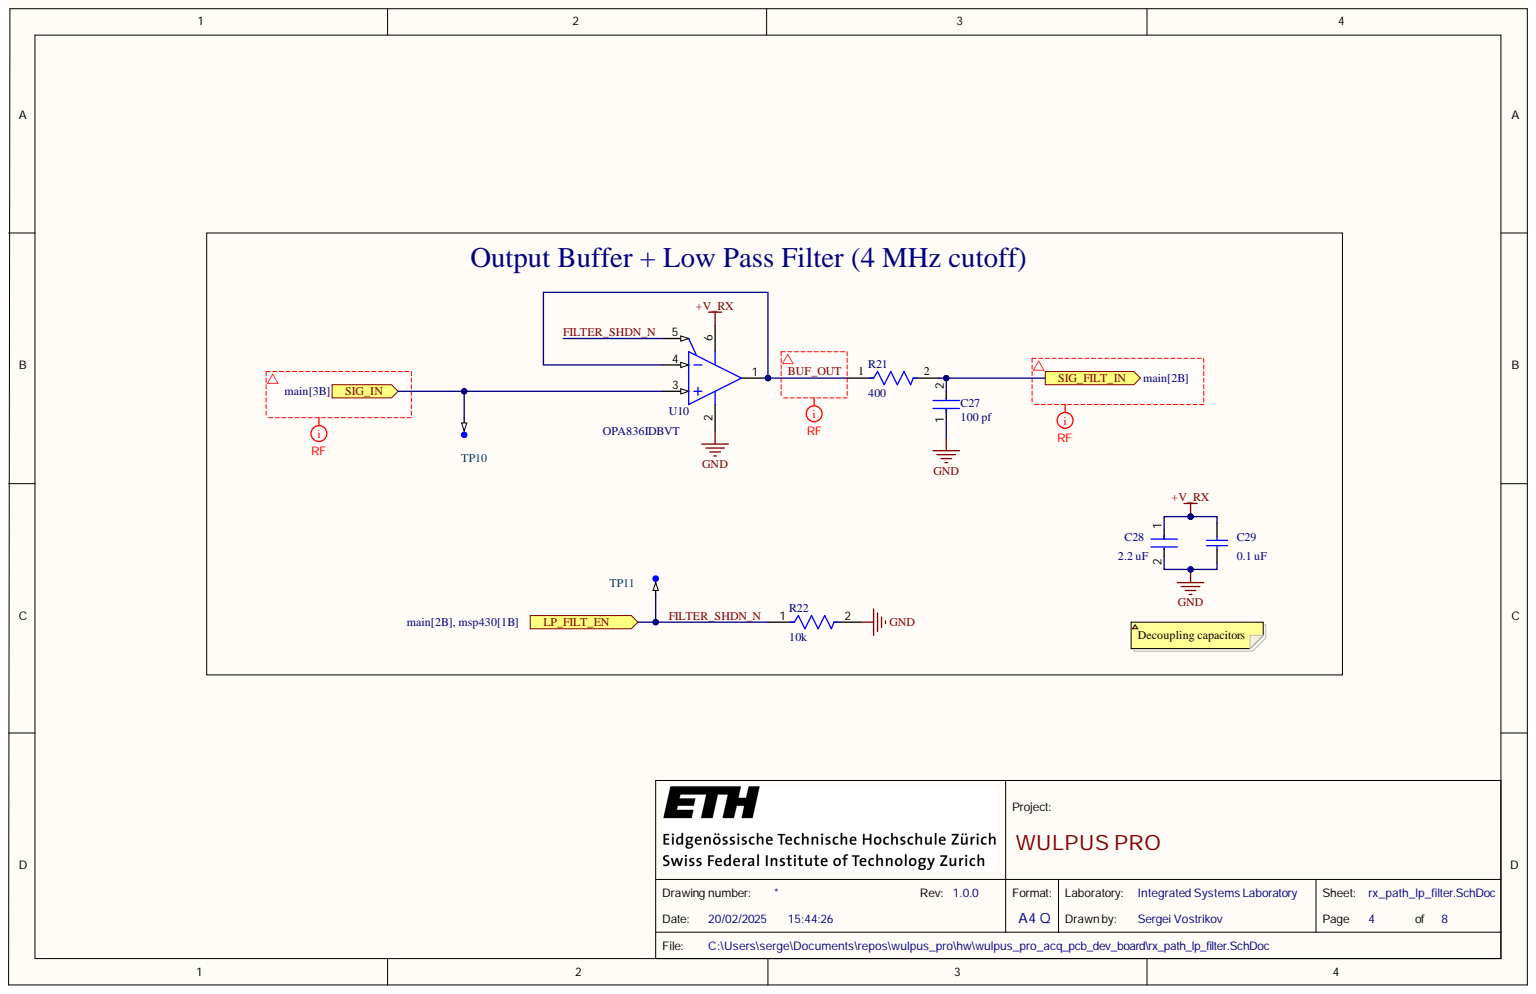
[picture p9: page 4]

Output Buffer + Low Pass Filter (4 MHz cutoff)

Project: WULPUS PRO

Drawing number: * Rev: 1.0.0 Date: 20/02/2025 15:44:26 | Format: A4 Q | Laboratory: Integrated Systems Laboratory Drawn by: Sergei Vostrikov | Sheet: rx_path_lp_filter.SchDoc Page 4 of 8

C:\Users\serge\Documents\repos\wulpus_pro\hw\wulpus_pro_acq_pcb_dev_board\rx_path_lp_filter.SchDoc

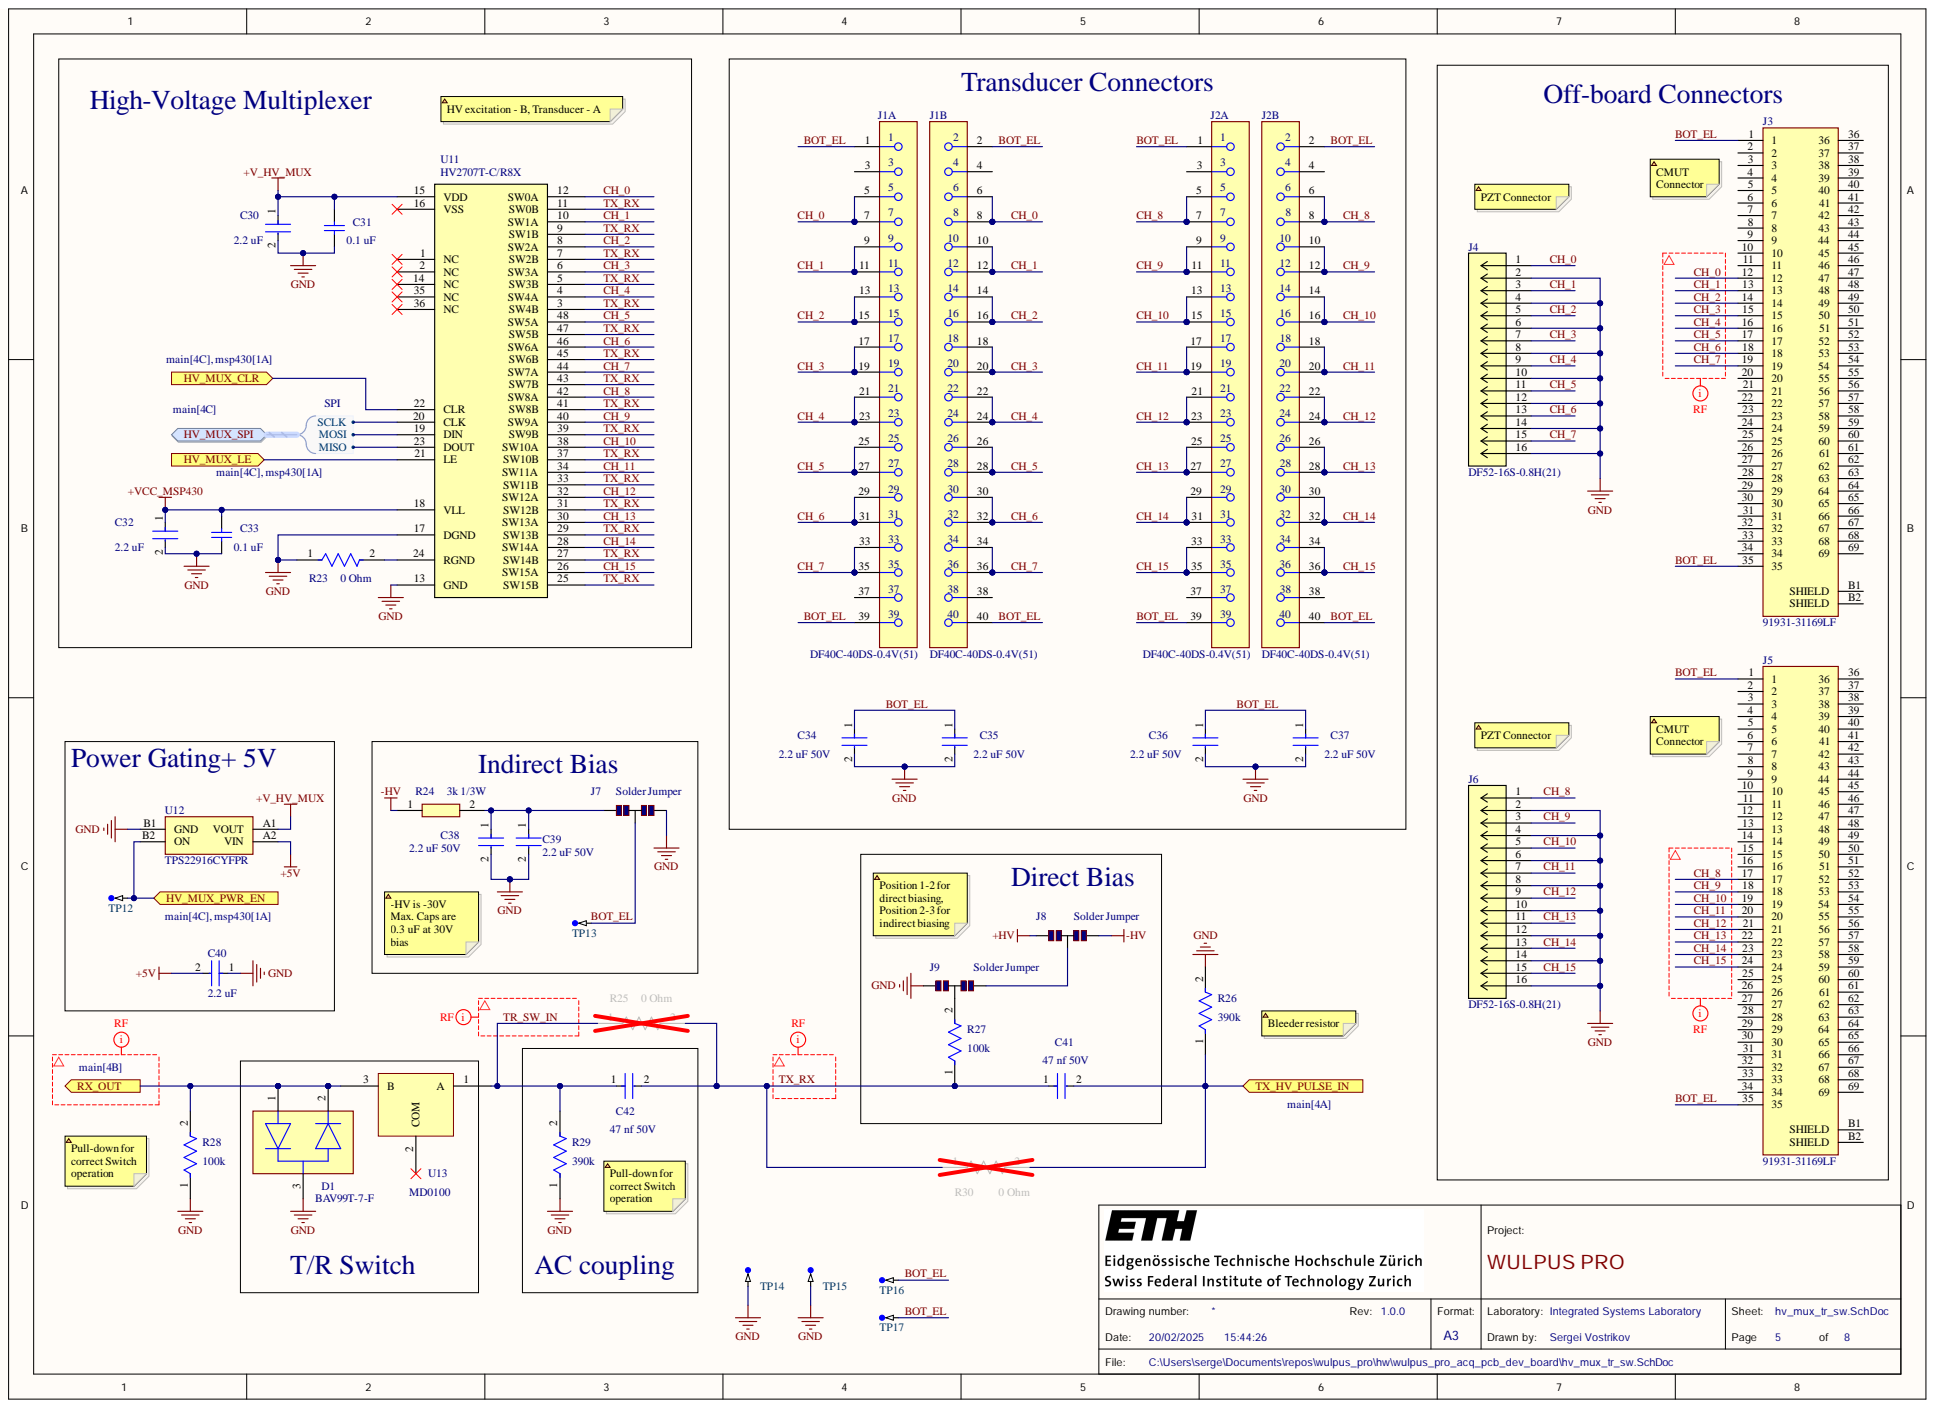
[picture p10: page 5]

Project: WULPUS PRO

hv_mux_tr_sw.SchDoc Page 5 of 8

C:\Users\serge\Documents\repos\wulpus_pro\hw\wulpus_pro_acq_pcb_dev_board\hv_mux_tr_sw.SchDoc

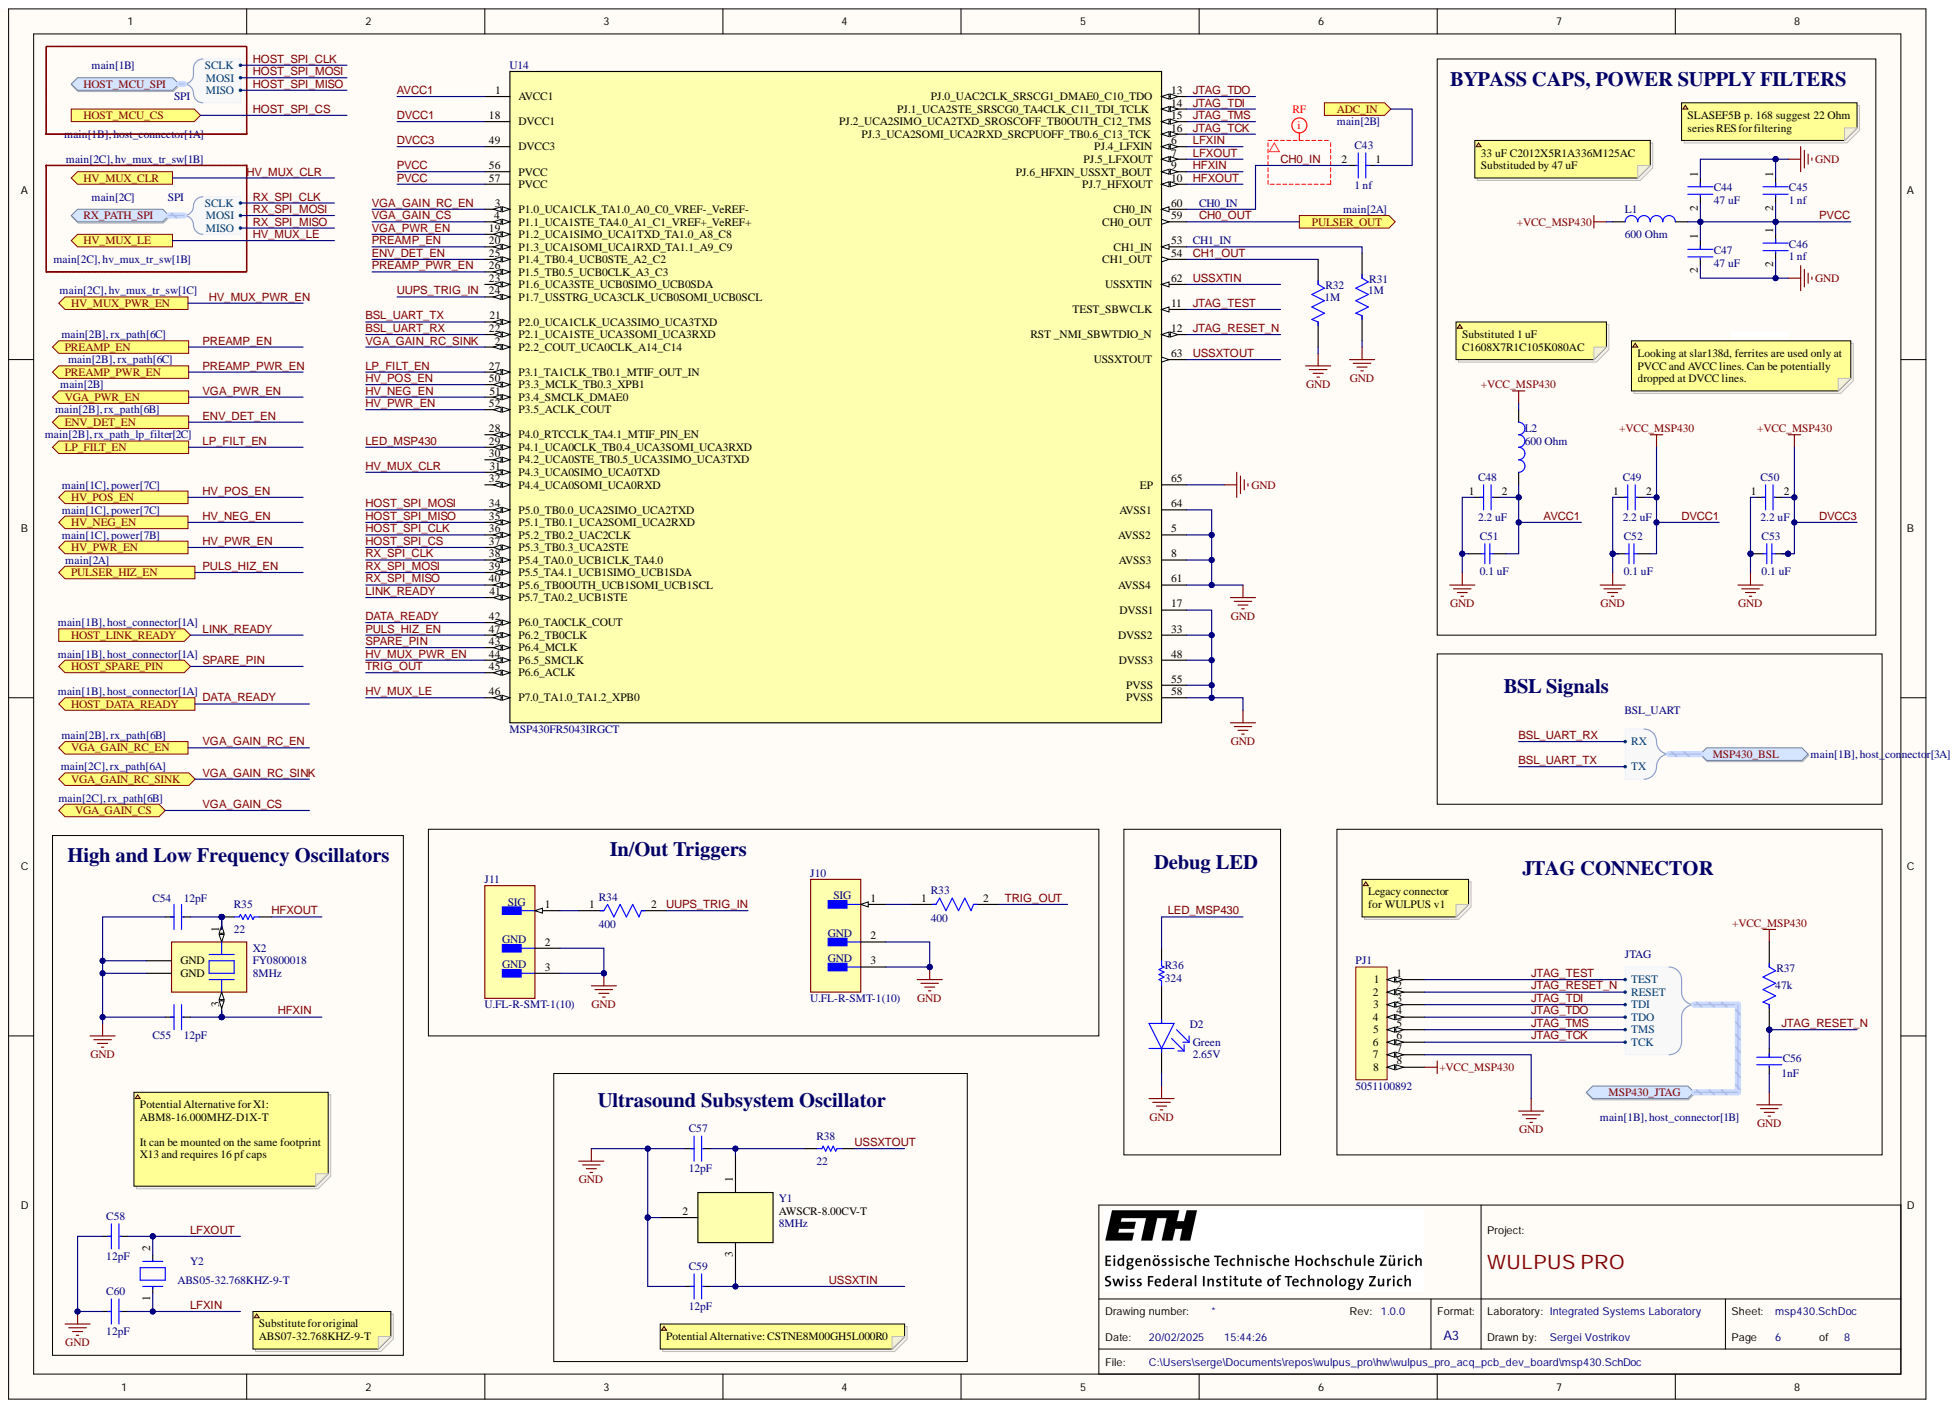
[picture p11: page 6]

BYPASS CAPS, POWER SUPPLY FILTERS

PVCC and AVCC lines. Can be potentially
dropped at DVCC lines.

JTAG CONNECTOR High and Low Frequency Oscillators

It can be mounted on the same footprint
X13 and requires 16 pf caps

Project: WULPUS PRO

msp430.SchDoc Page 6 of 8

C:\Users\serge\Documents\repos\wulpus_pro\hw\wulpus_pro_acq_pcb_dev_board\msp430.SchDoc

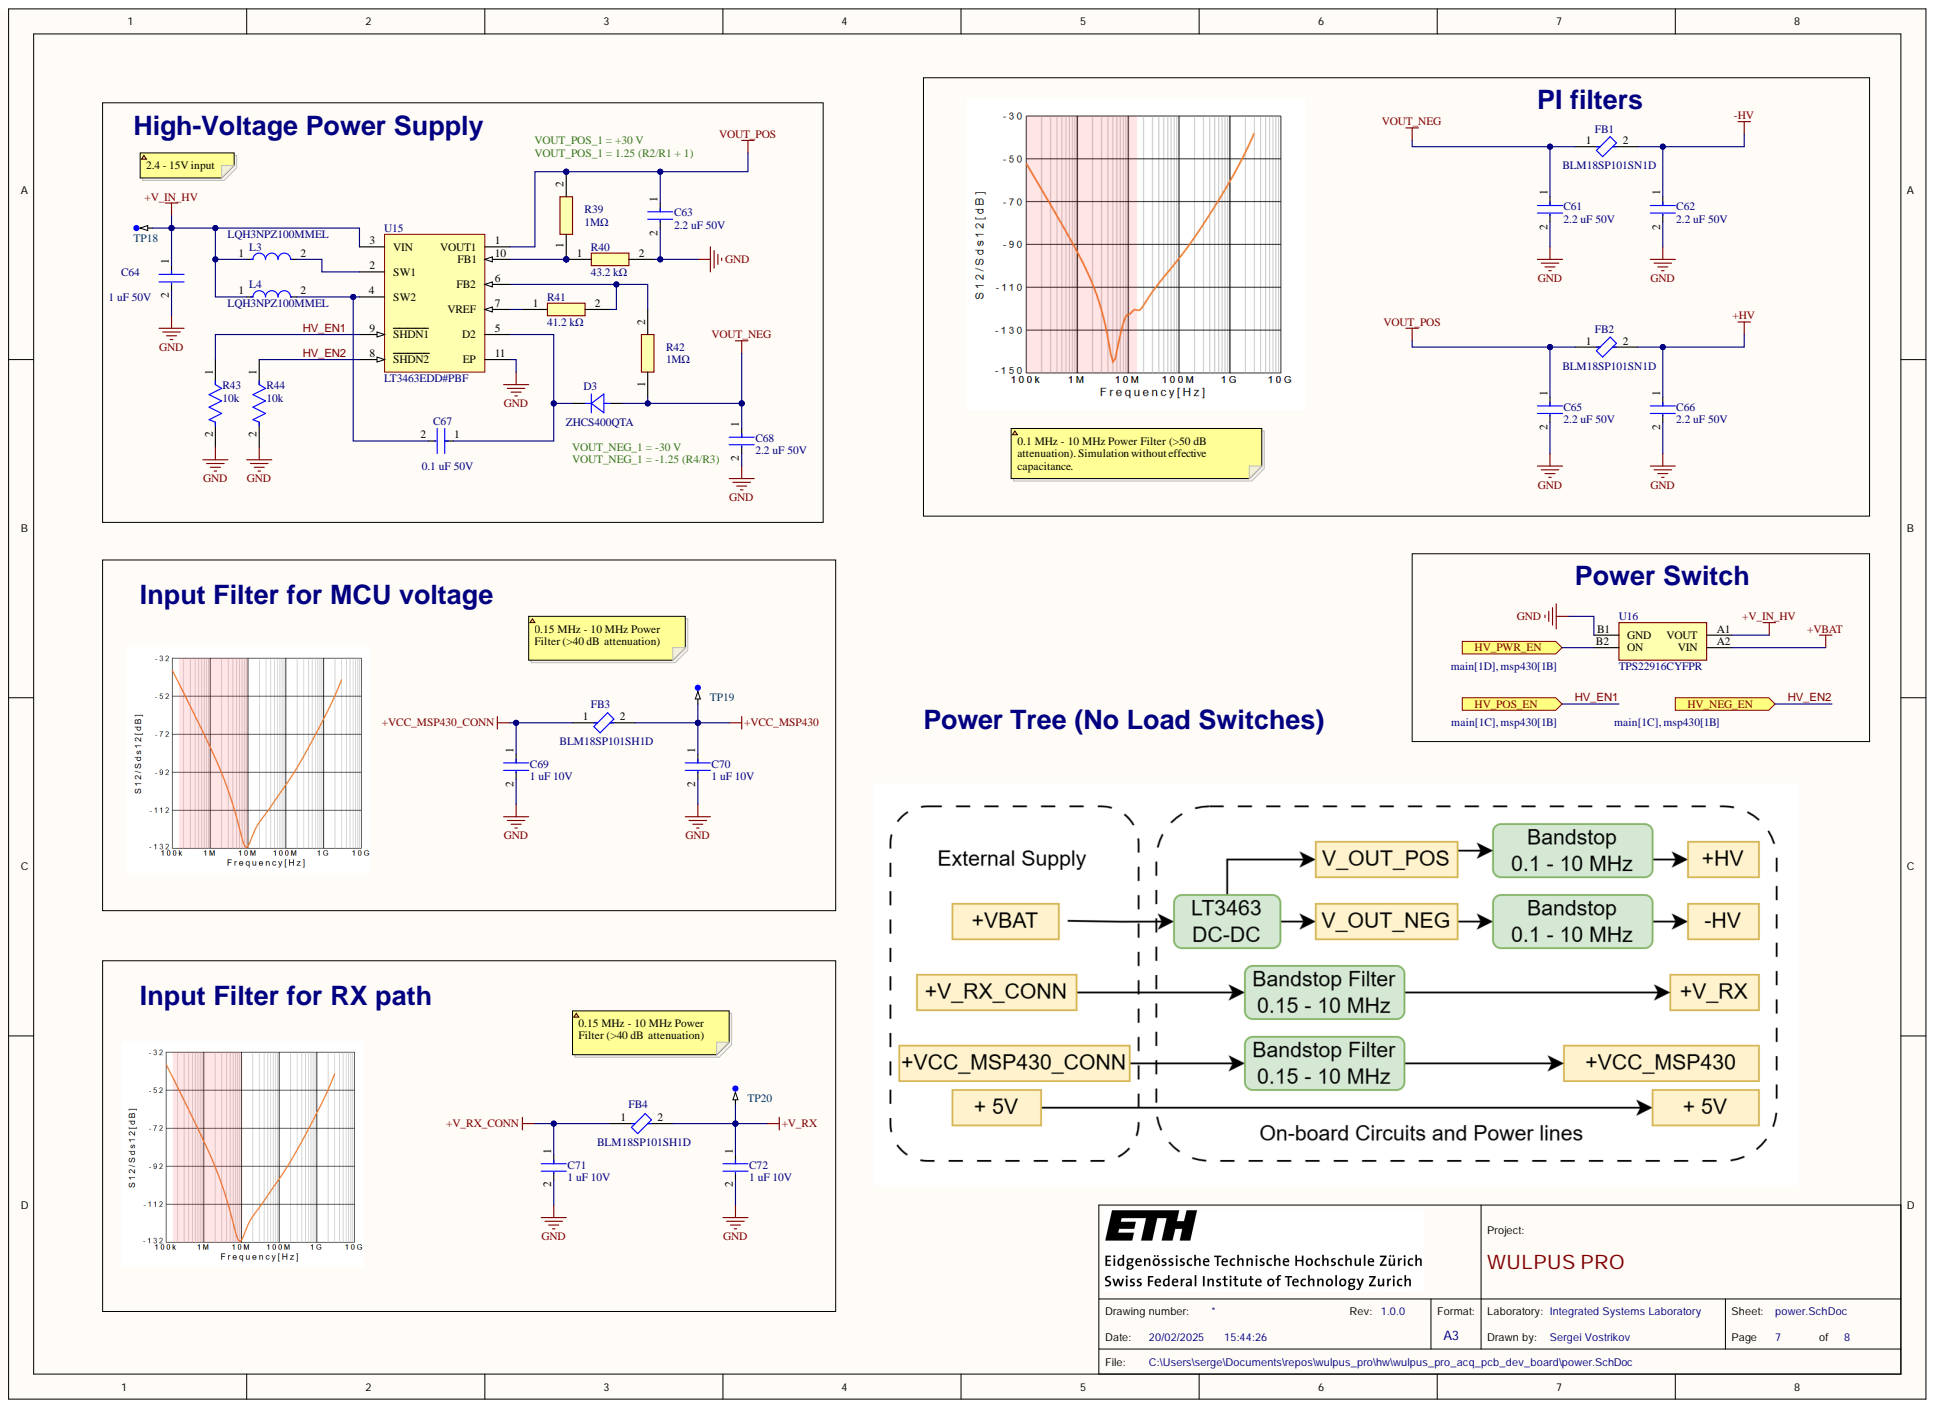
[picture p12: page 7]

High-Voltage Power Supply

SHDN1 9

HV_EN2 | | SHDN2 8

0.1 MHz - 10 MHz Power Filter (>50 dB
attenuation). Simulation without effective
capacitance.

Input Filter for MCU voltage

Input Filter for RX path

Project: WULPUS PRO

power.SchDoc Page 7 of 8

C:\Users\serge\Documents\repos\wulpus_pro\hw\wulpus_pro_acq_pcb_dev_board\power.SchDoc

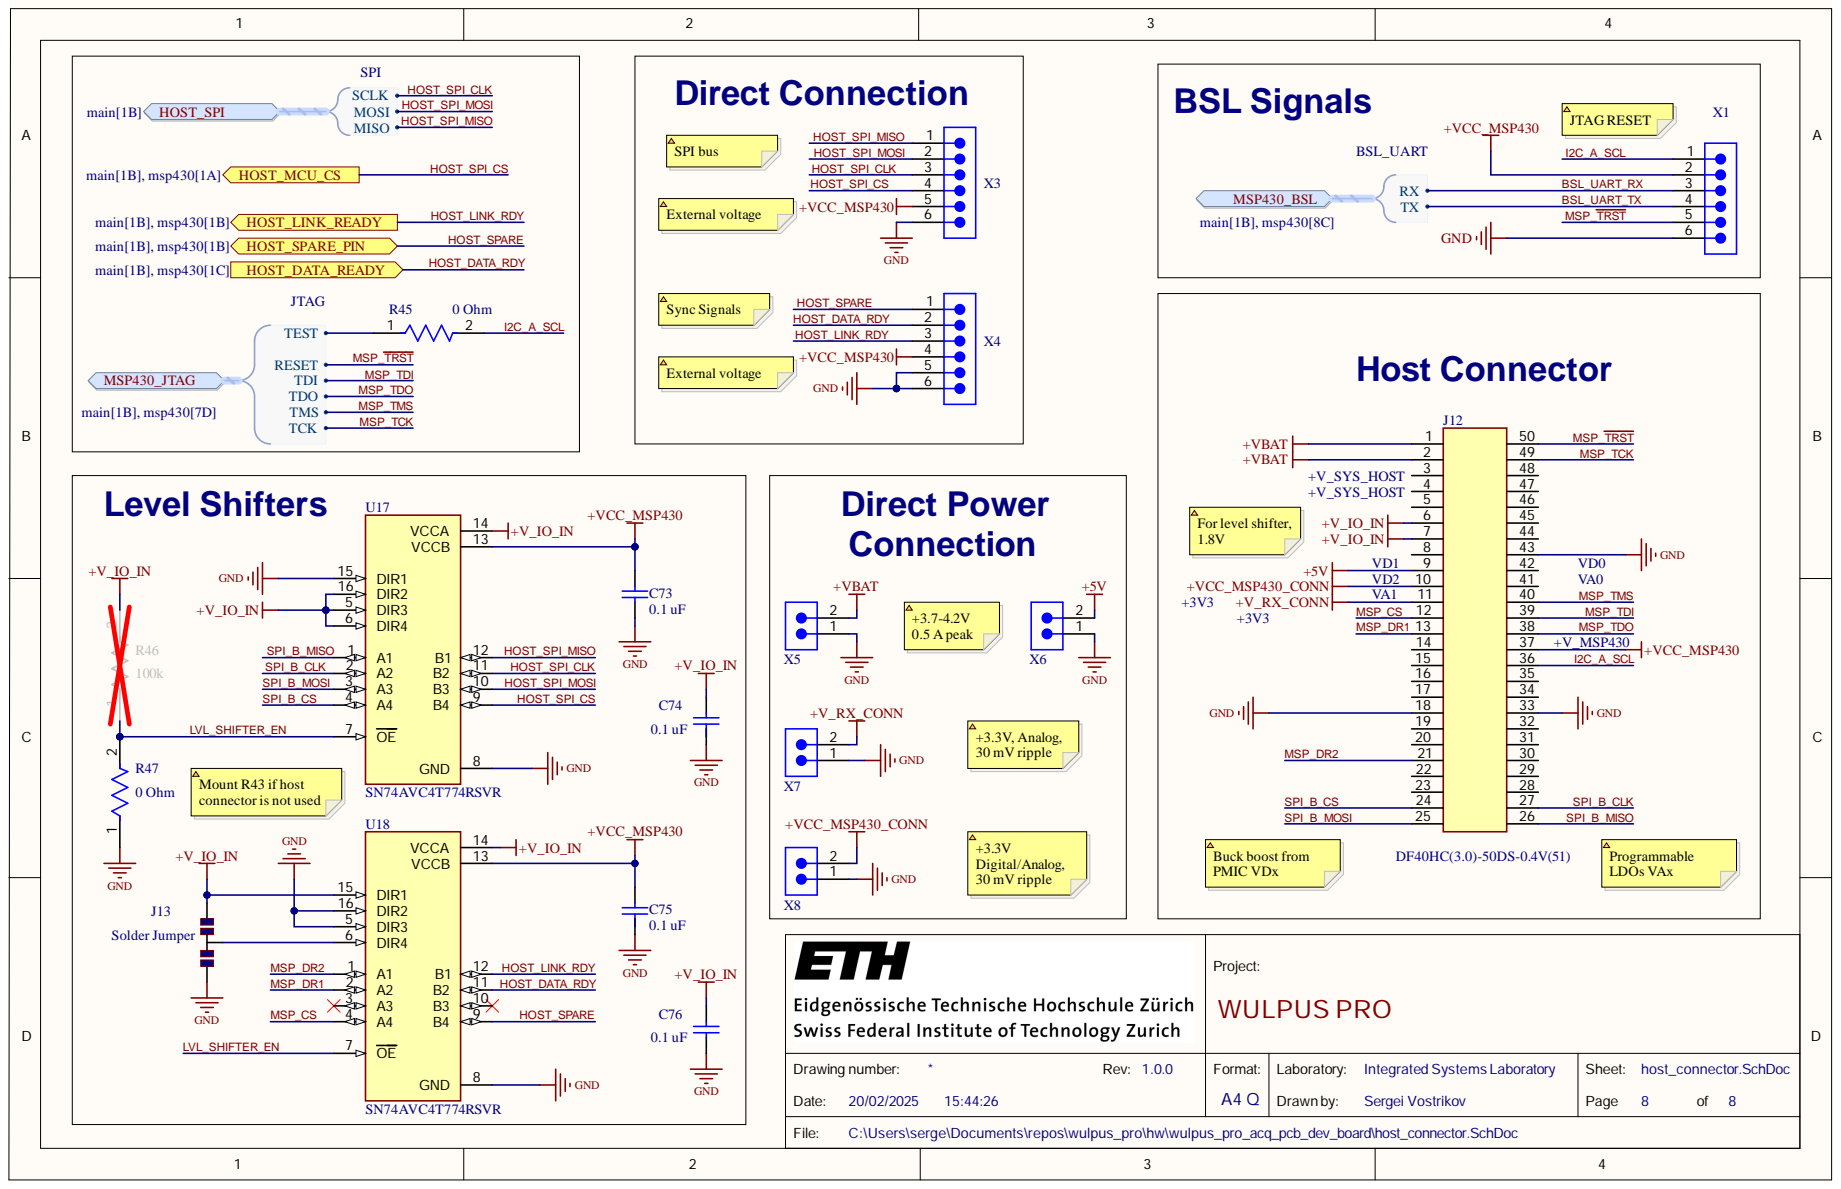
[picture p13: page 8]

Mount R43 if host
connector is not used

Project: WULPUS PRO

Drawing number: * Rev: 1.0.0 Date: 20/02/2025 15:44:26 | Format: A4 Q | Laboratory: Integrated Systems Laboratory Drawn by: Sergei Vostrikov | Sheet: host_connector.SchDoc Page 8 of 8

C:\Users\serge\Documents\repos\wulpus_pro\hw\wulpus_pro_acq_pcb_dev_board\host_connector.SchDoc


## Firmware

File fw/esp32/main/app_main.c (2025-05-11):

/* Wi-Fi Provisioning Manager Example

   This example code is in the Public Domain (or CC0 licensed, at your option.)

   Unless required by applicable law or agreed to in writing, this
   software is distributed on an "AS IS" BASIS, WITHOUT WARRANTIES OR
   CONDITIONS OF ANY KIND, either express or implied.
*/

#include <stdio.h>
#include <string.h>

#include <freertos/FreeRTOS.h>
#include <freertos/task.h>

// #include <esp_wifi.h>
#include <esp_event.h>
#include <esp_pm.h>
#include <esp_system.h>
#include <esp_timer.h>

#include <driver/gpio.h>
#include <driver/spi_master.h>

// #include "lwip/err.h"
// #include "lwip/sockets.h"
// #include "lwip/sys.h"
// #include <lwip/netdb.h>

#include "bsp.h"
#include "provisioner.h"
#include "mdns_manager.h"
#include "double_reset.h"
#include "commander.h"
#include "sock.h"

#include "helpers.h"

#define LOG_LOCAL_LEVEL ESP_LOG_INFO
#include <esp_log.h>

#define TCP_PORT_MUTEX_TIMEOUT pdMS_TO_TICKS(1000)
#define SPI_MUTEX_TIMEOUT pdMS_TO_TICKS(1000)
#define DATA_READY_TIMEOUT pdMS_TO_TICKS(1000)

static const char *TAG = "main";

socket_instance_t response_socket;
spi_device_handle_t spi = NULL;

TaskHandle_t tcp_server_task_handle = NULL;
TaskHandle_t data_handler_task_handle = NULL;

static QueueHandle_t gpio_evt_queue = NULL;

SemaphoreHandle_t data_ready_semaphore = NULL;
SemaphoreHandle_t tcp_port_mutex = NULL;
SemaphoreHandle_t spi_mutex = NULL;

bool transmits_enabled = false;

uint8_t spi_rx_buffer[CONFIG_WP_DATA_RX_LENGTH + HEADER_LEN];

static void tcp_server_task(void *pvParameters);
static void data_handler_task(void *pvParameters);

static void IRAM_ATTR data_ready_handler(void *arg)
{
    uint32_t gpio_num = (uint32_t)arg;
    xQueueSendFromISR(gpio_evt_queue, &gpio_num, NULL);
}

void app_main(void)
{
    ESP_ERROR_CHECK(bsp_init());

#if CONFIG_WP_DOUBLE_RESET
    // Check double reset
    bool reset_provisioning = false;
    ESP_ERROR_CHECK(double_reset_start(&reset_provisioning, CONFIG_WP_DOUBLE_RESET_TIMEOUT));
    if (reset_provisioning)
    {
        ESP_LOGI(TAG, "Double reset detected! Provisioning will be reset.");
    }
#endif

#if CONFIG_WP_ENABLE_PM
    // Configure power management (DFS and auto light sleep)
    esp_pm_config_t pm_config = {
        .max_freq_mhz = CONFIG_ESP_DEFAULT_CPU_FREQ_MHZ,
        .min_freq_mhz = 10,
        .light_sleep_enable = true,
    };
    ESP_ERROR_CHECK(esp_pm_configure(&pm_config));
#endif

    esp_log_level_set(TAG, LOG_LOCAL_LEVEL);

    // Initialize provisioner and thus wifi
    ESP_ERROR_CHECK(provisioner_init());

    // Initialize mDNS
    ESP_ERROR_CHECK(mdns_manager_init("wulpus"));
    ESP_ERROR_CHECK(mdns_manager_add("wulpus", MDNS_PROTO_TCP, CONFIG_WP_SOCKET_PORT));

    // Initialize GPIO
    gpio_config_t gpio_cfg = {
        .intr_type = GPIO_INTR_DISABLE,
        .mode = GPIO_MODE_OUTPUT,
        .pin_bit_mask = (1ULL << CONFIG_WP_GPIO_LINK_READY),
        .pull_down_en = GPIO_PULLDOWN_DISABLE,
        .pull_up_en = GPIO_PULLUP_DISABLE,
    };
    ESP_ERROR_CHECK(gpio_config(&gpio_cfg));
    ESP_ERROR_CHECK(gpio_set_level(CONFIG_WP_GPIO_LINK_READY, 0));
    ESP_ERROR_CHECK(gpio_sleep_sel_dis(CONFIG_WP_GPIO_LINK_READY));

    gpio_cfg.intr_type = GPIO_INTR_POSEDGE;
    gpio_cfg.mode = GPIO_MODE_INPUT;
    // gpio_cfg.pull_down_en = GPIO_PULLDOWN_ENABLE;
    gpio_cfg.pin_bit_mask = (1ULL << CONFIG_WP_GPIO_DATA_READY);
    ESP_ERROR_CHECK(gpio_config(&gpio_cfg));
    ESP_ERROR_CHECK(gpio_sleep_set_direction(CONFIG_WP_GPIO_DATA_READY, GPIO_MODE_INPUT));
    ESP_ERROR_CHECK(gpio_sleep_set_pull_mode(CONFIG_WP_GPIO_DATA_READY, GPIO_FLOATING));

    // Create semaphore
    gpio_evt_queue = xQueueCreate(10, sizeof(uint32_t));
    if (gpio_evt_queue == NULL)
    {
        ESP_LOGE(TAG, "Failed to create semaphore");
        return;
    }

    data_ready_semaphore = xSemaphoreCreateBinary();
    if (data_ready_semaphore == NULL)
    {
        ESP_LOGE(TAG, "Failed to create semaphore");
        return;
    }

    tcp_port_mutex = xSemaphoreCreateMutex();
    if (tcp_port_mutex == NULL)
    {
        ESP_LOGE(TAG, "Failed to create mutex");
        return;
    }
    spi_mutex = xSemaphoreCreateMutex();
    if (spi_mutex == NULL)
    {
        ESP_LOGE(TAG, "Failed to create mutex");
        return;
    }

    // Create data handler
    xTaskCreate(data_handler_task, "data_handler", CONFIG_WP_HANDLER_STACK_SIZE, NULL, CONFIG_WP_HANDLER_PRIORITY, &data_handler_task_handle);
    if (data_handler_task_handle == NULL)
    {
        ESP_LOGE(TAG, "Failed to create data handler task");
        return;
    }

    // Initialize interrupt
    ESP_ERROR_CHECK(gpio_install_isr_service(0));
    ESP_ERROR_CHECK(gpio_isr_handler_add(CONFIG_WP_GPIO_DATA_READY, data_ready_handler, (void *)CONFIG_WP_GPIO_DATA_READY));

    // Initialize SPI
    spi_bus_config_t spi_cfg = {
        .miso_io_num = CONFIG_WP_SPI_MISO,
        .mosi_io_num = CONFIG_WP_SPI_MOSI,
        .sclk_io_num = CONFIG_WP_SPI_CLK,
        .quadwp_io_num = -1,
        .quadhd_io_num = -1,
        .max_transfer_sz = CONFIG_WP_SPI_MAX_TRANSFER_SIZE,
    };
    spi_device_interface_config_t dev_cfg = {
        .clock_speed_hz = CONFIG_WP_SPI_CLOCK_SPEED,
        .mode = 1,
        .spics_io_num = CONFIG_WP_SPI_CS,
        .queue_size = 3,
        .cs_ena_pretrans = 16,
        .cs_ena_posttrans = 16,
    };
    ESP_ERROR_CHECK(spi_bus_initialize(CONFIG_WP_SPI_INSTANCE - 1, &spi_cfg, SPI_DMA_CH_AUTO));
    ESP_ERROR_CHECK(spi_bus_add_device(CONFIG_WP_SPI_INSTANCE - 1, &dev_cfg, &spi));

    ESP_ERROR_CHECK(gpio_sleep_set_direction(CONFIG_WP_SPI_CLK, GPIO_MODE_OUTPUT));
    ESP_ERROR_CHECK(gpio_sleep_set_pull_mode(CONFIG_WP_SPI_CLK, GPIO_PULLDOWN_ONLY));

    ESP_ERROR_CHECK(gpio_sleep_set_direction(CONFIG_WP_SPI_MOSI, GPIO_MODE_OUTPUT));
    ESP_ERROR_CHECK(gpio_sleep_set_pull_mode(CONFIG_WP_SPI_MOSI, GPIO_PULLDOWN_ONLY));

    ESP_ERROR_CHECK(gpio_sleep_set_direction(CONFIG_WP_SPI_MISO, GPIO_MODE_INPUT));
    ESP_ERROR_CHECK(gpio_sleep_set_pull_mode(CONFIG_WP_SPI_MISO, GPIO_FLOATING));

    ESP_ERROR_CHECK(gpio_sleep_set_direction(CONFIG_WP_SPI_CS, GPIO_MODE_OUTPUT));
    ESP_ERROR_CHECK(gpio_sleep_set_pull_mode(CONFIG_WP_SPI_CS, GPIO_PULLUP_ONLY));

    // Start provisioning
#if CONFIG_WP_DOUBLE_RESET
    ESP_ERROR_CHECK(provisioner_start(reset_provisioning));
#else
    ESP_ERROR_CHECK(provisioner_start(false));
#endif
    ESP_ERROR_CHECK(provisioner_wait());

    // // Print wifi stats
    // print_wifi_stats();

    // Start but suspend TWT
    provisioner_twt_setup();

    // Start TCP server
    xTaskCreate(tcp_server_task, "tcp_server", CONFIG_WP_SERVER_STACK_SIZE, NULL, CONFIG_WP_SERVER_PRIORITY, &tcp_server_task_handle);
    if (tcp_server_task_handle == NULL)
    {
        ESP_LOGE(TAG, "Failed to create server task");
        return;
    }

    ESP_LOGI(TAG, "Returning from app_main()");
}

static void tcp_server_task(void *pvParameters)
{
    ESP_LOGI(TAG, "TCP server task started");

    uint8_t rx_buffer[CONFIG_WP_SERVER_RX_BUFFER_SIZE];

    socket_instance_t listen_sock = sock_create();
    if (listen_sock.mutex == NULL)
    {
        ESP_LOGE(TAG, "Failed to create listen socket");
        vTaskDelete(NULL);
        return;
    }

    response_socket = sock_create();
    if (response_socket.mutex == NULL)
    {
        ESP_LOGE(TAG, "Failed to create response socket");
        vTaskDelete(NULL);
        return;
    }

    // Initialize and bind listening socket
    ESP_ERROR_CHECK(sock_init(&listen_sock));
    ESP_ERROR_CHECK(sock_listen(&listen_sock, INADDR_ANY, CONFIG_WP_SOCKET_PORT));

    // Initialize response socket
    ESP_ERROR_CHECK(sock_init(&response_socket));

    esp_err_t err = ESP_OK;
    while (1)
    {
        // Accept a connection
        err = sock_accept(&listen_sock, &response_socket);
        if (err != ESP_OK)
        {
            ESP_LOGE(TAG, "Failed to accept connection");
            continue;
        }

        provisioner_twt_suspend(1);

        // Clear data ready signal
        xSemaphoreTake(data_ready_semaphore, 0);

        bool run = true;
        while (run)
        {
            wulpus_command_header_t recv_header;

            // Receive command from the socket (blocking)
            size_t data_len = sizeof(rx_buffer);
            err = command_recv(&response_socket, &recv_header, rx_buffer, &data_len);
            if (err != ESP_OK)
            {
                ESP_LOGE(TAG, "Failed to receive header");
                continue;
            }

            switch (recv_header.command)
            {
            case SET_CONFIG:
                ESP_LOGI(TAG, "Received set config command");

                // FIXME: This could be made tidier in the connection callback, but it's the same in the nRF52 firmware
                ESP_ERROR_CHECK(gpio_set_level(CONFIG_WP_GPIO_LINK_READY, 1));
                ESP_LOGD(TAG, "Link ready signal set");

                // Wait for data ready signal
                if (xSemaphoreTake(data_ready_semaphore, DATA_READY_TIMEOUT) != pdTRUE)
                {
                    ESP_LOGE(TAG, "Failed to take data ready semaphore");
                    break;
                }

                uint8_t spi_tx_buffer[804] = {0};
                memcpy(spi_tx_buffer, rx_buffer, data_len);

                ESP_LOGD(TAG, "Configuration package (%u bytes):", recv_header.data_length);
                for (size_t i = 0; i < recv_header.data_length; i++)
                {
                    ESP_LOGD(TAG, "  0x%02X ", spi_tx_buffer[i]);
                }

                // Send configuration via SPI to the device
                spi_transaction_t tx = {
                    .length = 804 * 8,
                    .tx_buffer = spi_tx_buffer,
                    .rx_buffer = NULL,
                };
                if (xSemaphoreTake(spi_mutex, SPI_MUTEX_TIMEOUT) != pdTRUE)
                {
                    ESP_LOGE(TAG, "Failed to take SPI mutex");
                    break;
                }
                esp_err_t ret = spi_device_transmit(spi, &tx);
                xSemaphoreGive(spi_mutex);
                if (ret != ESP_OK)
                {
                    ESP_LOGE(TAG, "Error occurred during SPI transmission: %s", esp_err_to_name(ret));
                    break;
                }
                else
                {
                    ESP_LOGD(TAG, "Configuration package sent successfully");
                }

                break;
            case GET_DATA:
                ESP_LOGW(TAG, "GET_DATA is not implemented");
                break;
            case PING:
                ESP_LOGI(TAG, "Received ping command");
                // Send response
                wulpus_command_header_t response = {
                    .magic = "wulpus",
                    .command = PONG,
                    .data_length = 4,
                };
                err = command_send(&response_socket, &response, "pong", 4);
                if (err != ESP_OK)
                {
                    ESP_LOGE(TAG, "Failed to send ping response");
                    break;
                }
                break;
            case RESET:
                ESP_LOGI(TAG, "Received reset command");
                // Reset self
                esp_restart();
                break;
            case CLOSE:
                ESP_LOGI(TAG, "Received close command");
                // Exit loop
                run = false;
                break;
            case START_RX:
                ESP_LOGI(TAG, "Received start RX command");
                // Enable transmits
                transmits_enabled = true;
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

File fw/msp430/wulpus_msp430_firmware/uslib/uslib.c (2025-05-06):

/*
 * Copyright (C) 2025 ETH Zurich. All rights reserved.
 *
 * Author: Sergei Vostrikov, ETH Zurich
 *
 * Licensed under the Apache License, Version 2.0 (the "License");
 * you may not use this file except in compliance with the License.
 * You may obtain a copy of the License at
 *
 *      http://www.apache.org/licenses/LICENSE-2.0
 *
 * Unless required by applicable law or agreed to in writing, software
 * distributed under the License is distributed on an "AS IS" BASIS,
 * WITHOUT WARRANTIES OR CONDITIONS OF ANY KIND, either express or implied.
 * See the License for the specific language governing permissions and
 * limitations under the License.
 * 
 * SPDX-License-Identifier: Apache-2.0
 */

#include "uslib.h"

static msp_config_t config;
static bool config_updated = false;

void setNewUsConfig(msp_config_t *newConfig)
{
    config = *newConfig;
    config_updated = true;
    return;
}

bool confUsSubsystem(void)
{

    if (config_updated == false)
        return false;

    // Check if no active conversion is in progress
    if(UUPSCTL & USS_BUSY)
    {
        // Error: conversion is ongoing
        return false;
    }

    // Always triggered in SW
    // Future alternative - USSTRG (see datasheet)
    UUPSCTL = ASQEN + 0x00;

    // // Unlock SDHS register for configuration
    // SDHSCTL3 &= ~(TRIGEN);

    // // Configure SDHS Modulator Optimization
    // // (p. 614 of slau367p)
    // switch (config.pllOutFreq)
    // {
    //     case HSPLL_OUT_80_MHZ:
    //     case HSPLL_OUT_79_MHZ:
    //     case HSPLL_OUT_78_MHZ:
    //     case HSPLL_OUT_77_MHZ:
    //         SDHSCTL7 = MODOPTI3 + MODOPTI2; // 0xC
    //         break;
    //     case HSPLL_OUT_76_MHZ:
    //     case HSPLL_OUT_75_MHZ:
    //     case HSPLL_OUT_74_MHZ:
    //         SDHSCTL7 = MODOPTI3 + MODOPTI2 + MODOPTI0; // 0xD
    //         break;
    //     case HSPLL_OUT_73_MHZ:
    //     case HSPLL_OUT_72_MHZ:
    //     case HSPLL_OUT_71_MHZ:
    //         SDHSCTL7 = MODOPTI3 + MODOPTI2 + MODOPTI1; // 0xE
    //         break;
    //     default:
    //         SDHSCTL7 = MODOPTI3 + MODOPTI2 + MODOPTI1 + MODOPTI0; // 0xF
    //         break;
    // }

    // // Lock SDHS register for configuration
    // SDHSCTL3 |= (TRIGEN);

    // Calculate HSPLL Multiplier
    // (p. 481 of slau367p)
    // PLL out clk. freq = input clk. freq x (PLLM + 1)
    // The final output clk. freq. = PLL out clk. freq / 2

    uint16_t tempVar = (uint16_t) config.pllOutFreq;

    // Divide the frequency depending on the XTAL frequency
    switch(config.xtalFreq)
    {
        case HSPLL_XTAL_FREQ_4_MHZ:
            // x2 (see formula above) and then /4 => /2
            tempVar >>= 1;
            break;
        case HSPLL_XTAL_FREQ_8_MHZ:
            // x2 (see formula above) and then /8 => /4
            tempVar >>= 2;
            break;
        default:
            return 0;
    }

    tempVar--;
    // PLLM is 5 bits from 10 to 15.
    tempVar = (tempVar<<10);

    // If input frequency is > 6 MHz => set PLLINFREQ bit
    if(config.xtalFreq ==  HSPLL_XTAL_FREQ_8_MHZ)
    {
        HSPLLCTL = tempVar + PLLINFREQ;
    }
    else
    {
        HSPLLCTL = tempVar;
    }
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

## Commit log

2025-04-24 Added functions to control all power domains, successfully measured HV pulses and HV MUX artifact
2025-04-24 Added initialization of RX SPI MISO pin as input, fixed power consumption issue (30 mA current from MSP430 line by HV MUX to drive MISO line)
2025-04-30 Add base ESP32 project
    [partitions.csv]
2025-04-30 Move LED code into BSP
2025-04-30 Fix LED indications
2025-04-30 Add WiFi power optimizations (1.7mA idle without TWT)
2025-05-06 Cleaned polyCMUT adapter PCB
    [Bill of Materials-ActiveBOM.xlsx, PCB1.GBL, PCB1.GBO, PCB1.GBP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]
2025-05-08 Add power measurements
2025-05-09 Move power measurement into seperate script
2025-05-11 Update README of ESP32 firmware

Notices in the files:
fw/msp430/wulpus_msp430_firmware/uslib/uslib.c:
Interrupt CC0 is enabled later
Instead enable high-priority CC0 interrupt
